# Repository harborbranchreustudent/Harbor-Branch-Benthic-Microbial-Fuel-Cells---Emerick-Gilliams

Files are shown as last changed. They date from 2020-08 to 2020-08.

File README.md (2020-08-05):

# Harbor-Branch-Benthic-Microbial-Fuel-Cells---Emerick-Gilliams
This repository holds all information relevant to the Benthic Microbial Fuel Cell (BMFC) Project with Intern Emerick Gilliams and Dr. Jordon Beckler

I urge you to read through the Final Project Write Up before looking through the GitHub files.

All of the following information is present in the Final Project Write Up:
• Detailed Relevancy, Methods, and Results of Indoor BMFCs... 
• Detailed Methods and Results of Outdoor BMFCs...
• Materials, Procedures and Recommendations regarding building an Arduino Voltmeter and an Arduino Waterproof Enclosure...
• Materials, Procedures and Recommendations regarding building your own BMFC Design and deploying it indoors and outdoors...

On the GitHub, you will find the different variations of code for the Arduino Voltmeter that was custom created. The information regarding these files are all in the Final Project Write Up.

A quick summary of these files are: 
They are all for an Arduino Pro Mini 3.3V 8MHz. 
Voltmeter_SD_RTC2_Sleep_Mini is for a single input;
Voltmeter_SD_RTC2_Sleep_Mini_Double is for a double input;
Voltmeter_SD_RTC2_Sleep_Mini_Triple is for a triple input;
Voltmeter_SD_RTC2_Sleep_Mini_Double_Charging is to be used with a double input for charging and discharging tests (More information on this in the Write Up.);

Download the three folders DS3232RTC, Time, Streaming and place into your libraries folder in your Arduino folder in order to use the files above. 

On this GitHub is also a supply list that lists everything you need to recreate my project.There are also the files and images of the circuit diagrams for all of the relevant codes. Once again, these are explained further in the Final Project Write Up. 

If you have any questions please reach out to me at gilliamse@ufl.edu...

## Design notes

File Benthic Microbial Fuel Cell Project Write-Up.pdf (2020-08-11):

# Benthic Microbial Fuel Cells Project

### Summer, 2020

Author: Emerick Gilliams
Supervisor: Dr. Jordon Beckler

# Table of Contents

OVERALL PROJECT SUMMARY AND INTRODUCTION: | 3
MY INDOOR FUEL CELLS | 4
WHY CREATE INDOOR BMFCS? | 4
MY VARIABLES | 4
Why These Variables | 4
Container Setup | 5
DATA GATHERING AND ANALYSIS | 5
Daily Voltage Readings | 5
Other Data Collection | 5
RESULTS | 6
Daily Voltage Measurements | 6
Discharging Tests | 7
Charging Tests | 8
MY OUTDOOR FUEL CELLS | 9
DATA COLLECTION: | 9
RESULTS: | 9
MATERIALS: | 11
MATERIALS FOR A DEPLOYABLE FUEL CELL: | 11
The Electrode System | 11
Fuel Cell PVC Design | 12
MATERIALS FOR ARDUINO CIRCUITRY AND ENCLOSURE | 12
Arduino Circuitry | 12
Arduino Enclosure | 13
MATERIALS FOR FUEL CELL DEPLOYMENT | 14
Variables | 14
Indoor Deployment | 14
Outdoor Deployment | 15
PROCEDURES | 16
ARDUINO RELATED PROCEDURES | 16
Arduino Material Modifications | 16
Arduino Circuitry Construction | 17
Programing the Arduino | 19
Calibrating the Arduino Voltmeter | 22
Testing and Measuring with the Arduino Voltmeter | 22
Monitoring Multiple Fuel Cells | 22
Conducting Discharging and Charging Tests | 24
Finding the Active and Sleep Current of the Arduino Circuitry | 25
Powering the Voltmeter via Battery | 25
Building the Arduino Enclosure | 26
FUEL CELL RELATED PROCEDURES | 28
Creating a Deployable Fuel Cell | 28
Indoor Deployment | 31
Outdoor Deployment | 33

RECOMMENDATIONS | 35
GENERAL RECOMMENDATIONS | 35
Variable Selection | 35
Fuel Cell Design (Unchambered vs. Chambered) | 35
Deployment is Key | 35
INDOOR DEPLOYMENT RECOMMENDATIONS | 36
Data Collection and Analysis | 36
Polarization Curves | 36
Oscillating Tests | 36
CLOSING REMARKS | 38

# Overall Project Summary and Introduction:

Hello!

My name is Emerick Gilliams, and I am a rising junior studying chemical engineering at the University of Florida. During the summer of 2020, I was taken on as a renewable energy intern at Harbor Branch Oceanographic Institute where I worked remotely on benthic microbial fuel cells (BMFCs).

BMFCs are an emerging option for renewable energy. BMFCs utilize microbes in the sediment of the benthic layer in a body of water to create an electric current as the microbes oxidize organic and inorganic matter. This creates a redox gradient between the anoxic sediment and oxic water.

The importance of this research and all research with BMFCs strongly relates to oceanographic research, as BMFCs are being investigated as a possible power source for subsea sensors. BMFCs are currently being used as battery substitutes and battery chargers for offshore dataloggers and sensors. Successfully making BMFCs a consistent power source would reduce the costs for device deployment, maintenance, and replacement, which happens to be some of the most expensive portions of marine research.

The overall goal of my project is to explore the capabilities of small-scale BMFCs. During my project, I have created ten indoor BMFCs using sediment and water samples from a nearby lake. I have been testing various sets of three variables: salinity, BMFC design, and addition of carbon-based additives. My project has shown that with even a fuel cell design size of a few inches, harvestable power is accomplishable.

During this research, I have also been working with Arduino circuitry to create a battery-powered device that can monitor the voltage of a fuel cell while recording that data to a micro SD card. This device can monitor up to six BMFCs for about 100 days while connected to a battery. Various code for the device can be found on the projects GitHub: Click Here... (https://github.com/harborbranchreustudent/Harbor-Branch-Benthic-Microbial-Fuel-Cells---Emerick-Gilliams)

For the conclusion of my project, three BMFCs were constructed in situ in a nearby lake and was monitored by my Arduino circuit in a waterproof enclosure. The data was analyzed after the completion of the program.

In this document, you can find information regarding:

- Materials required to make anything in my project….
- The procedures I created for my project…
- Detailed write-ups and data on each part of my project…
- Recommendations for anyone looking to follow in my footsteps…

Let us begin!

# My Indoor Fuel Cells

This part of the document is dedicated to my indoor fuel cells used in my project from the summer of 2020.

You will find the reason why I constructed these, the variables I used, how I collected data, and the results from that data.

For how I constructed these and pictures what they look like, check the procedures section.

### Why Create Indoor BMFCs?

There are a couple reasons why you would want to make indoor BMFCs.

The main reason is to control variables you cannot control in the environment. For example, one of the variables I tested was the effects of salinity. I would have never been able to do this if I were setting up my BMFCs in situ. Adding salt (or chemicals if you want to test the effect of that) can and will affect the environment you are testing in. Furthermore, do you know how much salt would be needed to change the salinity of an entire body of water? The only reasonable option for certain variables would be to create an isolated and easily changeable environment; Hence, create yourself a set of indoor BMFCs!

Of course there are other reasons, such as not having access to a good body of water to test in or wanting to test multiple variables at the same time; however, the main benefit is creating an isolated and changeable place to deploy your BMFCs.

### My Variables

During my project, I tested three different variables:

1. Salinity
2. Fuel Cell Design
3. Carbon-Based Additives

Why These Variables…
We tested the only two levels of salinity: freshwater from a lake and simulated ocean water. The simulated ocean water was taken from the same sample as the freshwater except for the addition of sea salt in the ratio of salt-to-water that would be found in the ocean. These two levels were chosen since most BMFCs were deployed in the ocean, and the nearest body of water to the location of the project at the time was a lake. An interesting project could be created around testing multiple levels of salinity though!

We also only tested two different fuel cell designs. The designs were the same excluding the fact that one had a chambered anode and one had an unchambered anode. This was done since these are the two classifications of BMFC design. See the

Fuel Cell Related Procedures regarding what these designs looked like.

The final variable was the addition, or non-addition of carbon-based additives to the bottom of the fuel cell container. This was done to see if the additives would encourage bacteria growth at a quicker pace, leading to a stronger voltage, than if no additive were added.

Container Setup…
I set the variables up in the following five combinations with two replicates each:
1. Freshwater/Chambered Design/Additive
2. Ocean Water/Chambered Design/Additive
3. Ocean Water/Chambered Design/No Additive
4. Ocean Water/Unchambered Design/No Additive
5. Ocean Water/Unchambered Design/Additive

You may be asking why I only had one freshwater group. The reason for this is I had eight possible combinations of variables, and I wanted to have two replicates each. One of the downsides of indoor BMFCs is you must have the space to place them. I only had the space for ten fuel cells, so three possible variable combinations had to be discarded.

After review, it was obvious that salt water would be a better environment for BMFCs due to the increased ionization in the water around the BMFCs. Due to this project being remote and the desire to strong results, Dr. Beckler and I decided to do mostly saltwater fuel cells.

### Data Gathering and Analysis

Daily Voltage Readings…
The main data that I gathered during my project was the daily voltage readings using a multimeter with leads connected to the anode and cathode. This was done twice a day at 10 AM and 4 PM. I find that this was unnecessary and that once a day is sufficient for future projects. These numbers gave an idea on how developed the redox gradient was at the time of measurement.

You can expect anywhere between 400 mV and 600 mv for a strong BMFC. In even the most ideal settings, the strongest redox potential you will see is 1.2V, so do not be disappointed by low voltages! Some of my fuel cells began with a negative voltage and slowly moved to positive over time. I began testing my cells the day after they were constructed, and I was already getting some interesting results.

Other Data Collection…
There are other tests you can run to gather data from as well. In the results section, there are some graphs regarding what I called “discharging” and “charging” tests. In the discharging test, the cathode and anode were set in series with a resistor. The voltage was monitored over a period and then plotted to observe the behavior of the fuel cells when discharging. This process is actually very important for constructing a polarization curve, something I never had the opportunity to do. See the Recommendations for more information on polarization curves.

The charging test was the exact opposite of this. The fuel cell would be discharged completely by touching the cathode and anode together, then the fuel cell would be monitored while the voltage increased back to its current high point, which is the same as that days daily measurement voltage values.

Both these tests can be done with the custom-made Arduino circuit and the “Voltmeter_SD_RTC2_Sleep_Mini_Double_Charging_Test” code. This code will monitor the fuel cell and record a measurement every 10 seconds. Make sure to calibrate and test on batteries to make sure it is accurate!

One test I never conducted but is very interesting to conduct would be an oscillating circuit. See the Recommendations.

### Results

Daily Voltage Measurements…
The following graph shows the daily measurements taken twice a day. Although some fuel cells started in the negative, a large majority of the fuel cells showed strong steady growth over the testing period. The highest points are in the low 600 mV range. The downward spike of the highest performing fuel cells near 7/7/20 was due to testing done on the cells that lowered the voltage temporarily. The three worst performing fuel cells were salvaged at a certain point as the materials were needed to construct the three in situ fuel cells used later in the project. This is seen in both graphs.

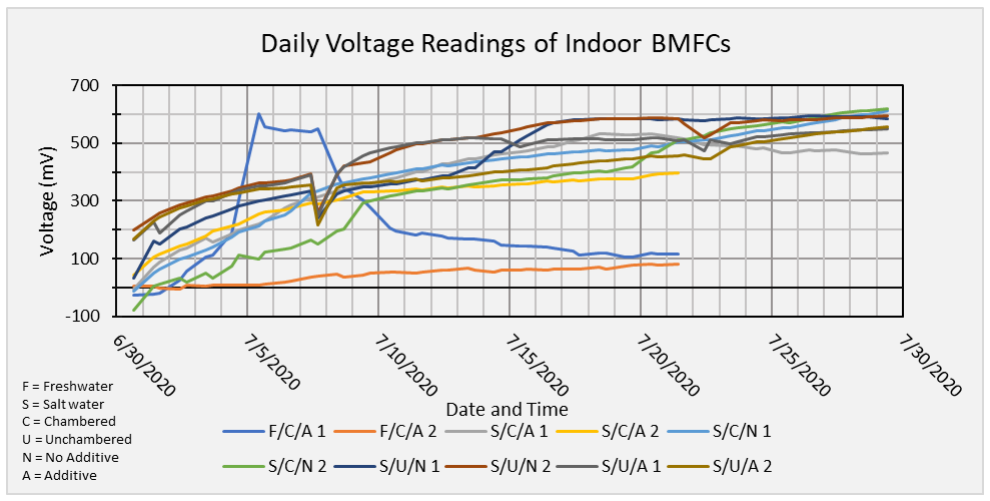
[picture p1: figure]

The following graph shows the daily measurements, but the replicates are grouped and averaged into their variable sets. From this you can see that the freshwater cells are the least consistent, while the saltwater cells are all consistently strong and steadily growing. This is most likely due to the increased ionization in the fuel cells with saltwater. The simple conclusion is saltwater fuel cells are stronger and a better option than freshwater.

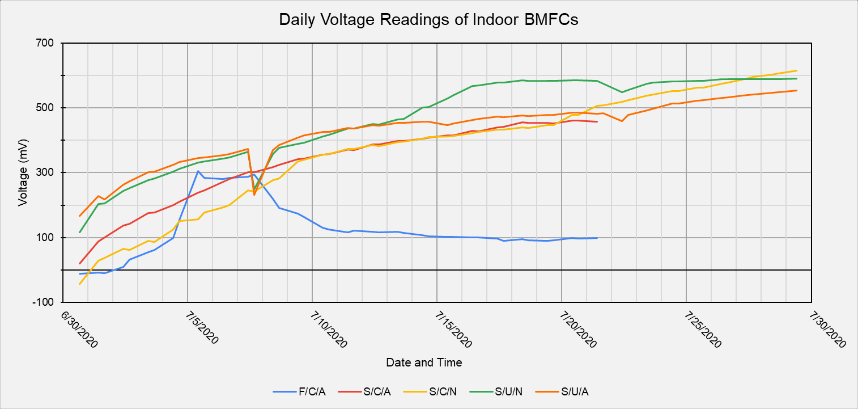
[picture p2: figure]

You can also see that unchambered vs chambered are generally the same, but with the slight advantage to the unchambered designs. This leads to the conclusion that the real variable here is ease of deployment. The easy the design is to deploy, the better chance the electrodes will be setup properly. The unchambered design is extremely easy to deploy in an indoor fuel cell, which many have given it the slight advantage it is shown to have. The chambered design would be easier to deploy in situ since the sediment in situ is much more compact, making it more difficult for an unchambered design to pierce the sediment.

The final variable, the carbon-based additive, seems to have little to no effect on the overall fuel cell voltage over longer periods of time; However, if you look at the first two weeks of deployment, you can see slight advantages to the fuel cells with additive. Coincidentally, the additive used was a 14-day slow-release vacation fish food. There may or may not be a connection. More testing needs to be done. There is no negative to adding an additive, only a possible benefit in having higher voltages earlier on. I would recommend the use of an additive if possible.

Discharging Tests…
This data was taken by placing a 20k Ohm resistor in series with the cathode and anode. The voltage was then measured across the resistor for 30 minutes and plotted. The four strongest fuel cells were fuel cells 7-10, which is why they were chosen for this test.

As you can see, the fuel cells will rapidly lose their charge and then stabilize at a lower voltage after a certain period. That stabilization voltage is the value needed to construct a polarization curve, which was not known to me at the time of the test. See the Recommendations section for more information.

The starting voltage is purely dependent on how developed the fuel cell is. The starting voltages coincide with the daily voltage reading of the day of the test.

This test was taken by recording a multimeter, but if you would like to do a test like this, use the code that is described in the “Other Data Collection…” section.

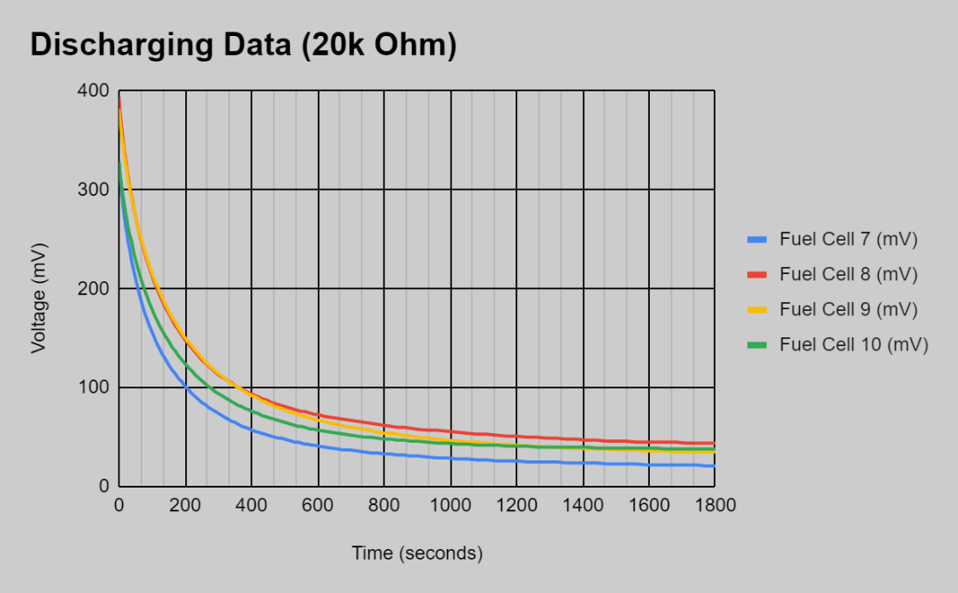
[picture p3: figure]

Charging Tests…
This data was taken by the code described in the “Other Data Collection…” section. The two of the strongest fuel cells at the time of testing was Fuel Cell 7 and 9. They were also chosen in a pair due to their proximity on the physical workstation.

As you can see, the charging behavior is very similar to the discharging behavior, as there is rapid change in the beginning and slow change as time goes on.

The test was stopped after 10 hours but could have continue to reach a better stabilizing voltage.

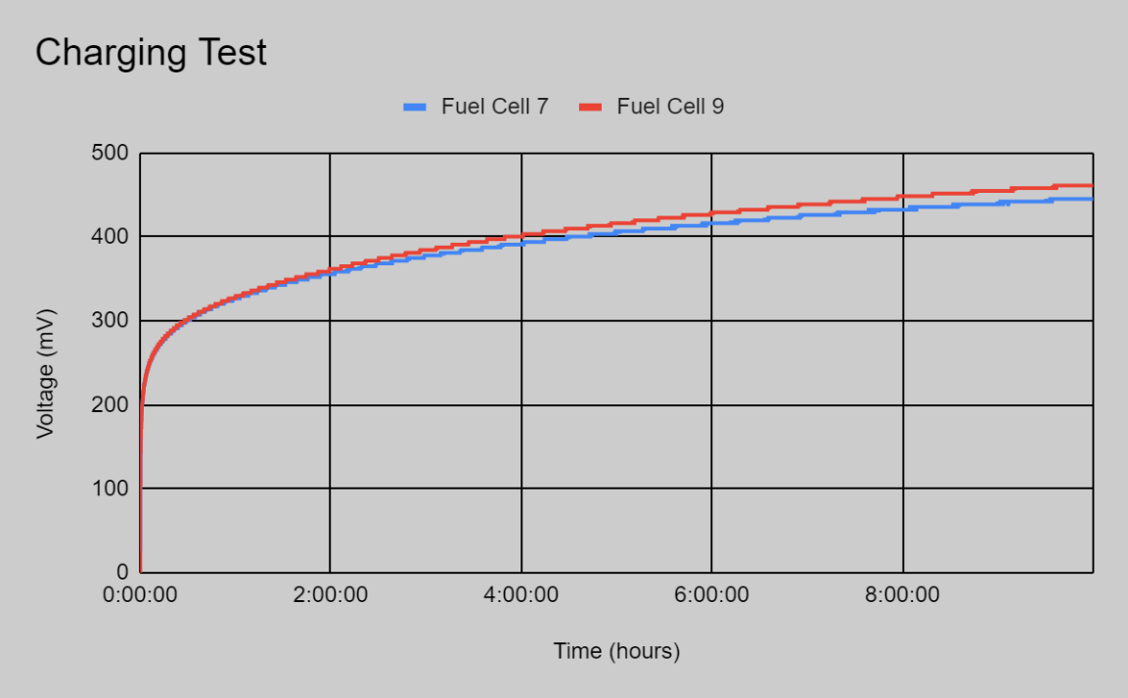
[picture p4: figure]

# My Outdoor Fuel Cells

### Data Collection:

Three fuel cells were deployed in a lake near me at the time. These fuel cells were being monitored by the custom-made device that is described further in the document. The fuel cells were deployed for slightly under a week before they were retrieved.

The device measured the voltage in mV every 10 minutes for the entire time. This data was transcribed onto a micro SD card for later analysis.

### Results:

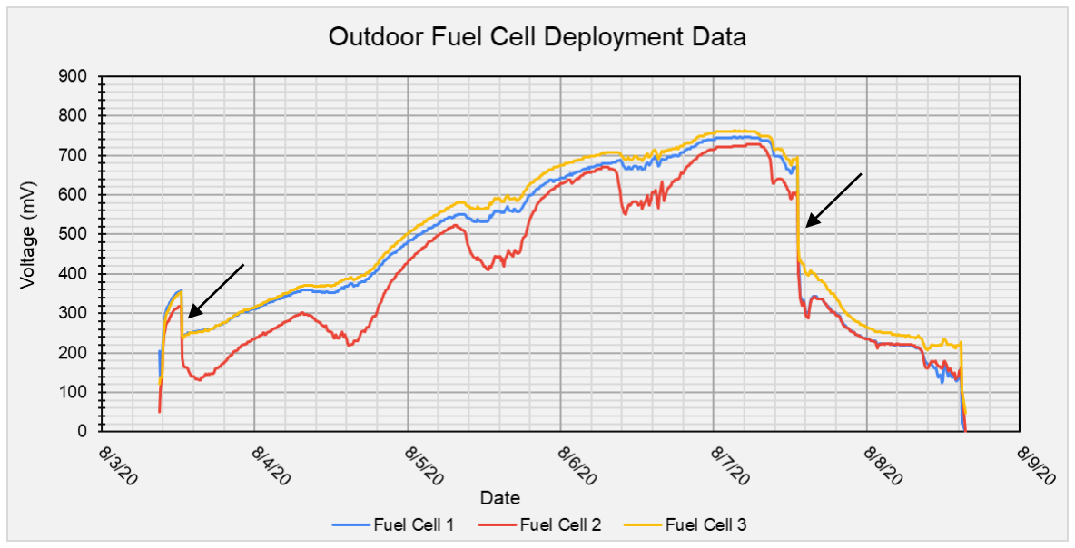
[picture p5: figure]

The graph above is the data for the outdoor deployment.

The first thing to discuss are the issues with deployment and how it affected the data.

I checked the state of the fuel cells every 1-2 days. When I went to check a day after deployment, Fuel Cell 2 was floating. I decided against redeploying the cell for these reasons.

1. I was uncertain if the data collector was fully operating due to a previous deployment issue.
2. if the measuring device was operating correctly, I did not want to disturb the sediment and affect the data collection.
3. I had two more, so I considered losing one was not an issue.

A few days after Fuel Cell 2 became dislodged, Fuel Cell 1 also began to float. You can see the effect of these changes on the voltages when looking at the two black arrows on the plot. The left most arrow is showing when Fuel Cell 2 dislodged, and the right arrow is Fuel Cell 1.

Now, why are the voltages all about the same and follow the same patterns even though fuel cells were dislodging?

I believe this is due to the concept that when multiple BMFCs are in the same body of water, they act as one BMFC.

As you can see, on the day Fuel Cell 2 dislodged, the red line dipped the strongest and was always under the other two lines. It also affected the overall voltage growth as you can see all the lines were increasing at a high rate in the beginning, then that rate decreased after the first dislodge. As time went on the yellow and blue lines both stayed about the same, with the red line being consistently worse.

It appears the lines were going to plateau at around 800 mV when the other fuel cell dislodged causing the voltage to drop significantly again. The overall plateau also decreased to around 200 mV. Furthermore, the fuel cell that dislodged next (Fuel Cell 1) then joined the red line and was the same until they were pulled from the sediment.

Another interesting thing that happens is every day at the same time there are periods of instability in the voltage. Furthermore, both fuel cells dislodged at a time during this instability. My guess is it has to do with the movement patterns of life in the lake. It makes sense that an increased amount of movement around the BMFCs would affect the voltage. It also makes sense that increased movement around the BMFCs could have jostled them enough to dislodge them from the sediment.

Interesting conclusions:

1. Supporting evidence that all BMFCs in a single body of water act as one BMFC.
2. If a BMFC dislodges, it will still hold a voltage, but one slightly lower than the ones still in the sediment
3. The amount of BMFCs in the sediment determines the overall maximum voltage.
4. If all fuel cells stayed in place, we could have gotten a value well over a volt in all cells, which is very interesting since the highest we saw in a month of indoor testing in environments with salt and additives is only around 625 mV.
5. Movement of life around the fuel cells could have cause periods of instability.
6. Make sure future BMFC designs are not buoyant to avoid unintentional dislodges.

# Materials:

All materials that are listed can be found in the Supply List.

This section is divided into categories for each part of the project, so some materials are listed multiple times if needed for different sections. Make sure you double check to not order things multiple times!

That supply list will give you an estimated cost for each item suggested, and a link or description of where you can find one!

For the sake of simplicity, we are going to use the symbol X to represent the number of BMFCs you would like to create.

For example, in my project X = 10.

If you see an [X * #] that is the quantity needed. No brackets imply 1.

### Materials for a Deployable Fuel Cell:

The Electrode System…
We are first going to list the materials for what I call the “electrode system” (For me, X = 10):
1. [X * 2] Electrodes
a. I used Carbon Fiber Brushes from Mill-Rose. I highly recommend these electrodes if your budget allows it. I used 2-inch brushes with 1-inch bristle length and 1-inch bristle radius
2. Electrical Wire
a. If you have the chance, get two colors! Black and red works perfectly!
3. Soldering Kit
a. The one I linked came with wire strippers and tweezers; if you decide to buy a different one, purchase these as well.
4. Wire Quick Connect Kit
5. Epoxy
6. Heat shrink tubing
7. Heat Gun
8. Multimeter
a. Test your connections every time you solder, epoxy, or connect wires!!!!
9. Pack of AA batteries
a. Use these with your multimeter or Arduino to test your connections or code/circuit.
10. Rosin Core Solder
a. In the Arduino Purchase section...
11. Painters Tape
12. Cling Wrap
13. Small zip ties
14. Pliers.

15. Some type of PVC to hold your electrodes (I used the ¾ inch PVC)
a. Mine is listed in the Fuel Cell PVC Design Section
16. Cardboard from boxes items came in

These materials are all highly recommended and should be purchased if you want to recreate the project.

Fuel Cell PVC Design…
These materials are for the PVC housing you that hold your electrodes system.

Depending on the design you chose, this will be different. I listed my materials if you wish to replicate my design exactly. See the Recommendations section…

For my 10 fuel cells, I had 6 chambered designs and 4 unchambered designs.

Here are the materials I used for my unchambered design (X = 4):
1. 3/4-inch diameter PVC pipe segment
2. [X] 3/4 elbow PVC pipe
a. I recommend using a vertical coupling if you have enough space in the enclosure. I used the elbows, so they are what are listed.
3. PVC pipe cutter

Here are the materials I used for the chambered design (X = 6):
1. 3/4-inch diameter PVC pipe segment
2. [X] 3/4 elbow PVC pipe
3. PVC pipe cutter
4. 3-inch diameter PVC pipe segment
5. [X] 3-inch x 1.5-inch PVC Coupler
6. [X] 1.5-inch x 3/4-inch PVC Bushing
7. Hacksaw
8. Sandpaper (The coarser the paper, the better.)

Once again, all these materials are subject to change if you use a different design.

### Materials for Arduino Circuitry and Enclosure

Arduino Circuitry…
1. Micro SD Card reader
a. Needed for the circuit to save the data it is monitoring
2. Micro SD Card
3. M-F, F-F, M-M Wires Kit
a. Needed for certain connections. Does not hurt to have extra wires either.
4. Pre-Formed Jumper Wire Kit
a. Needed for most connections. Keeps breadboard clean and easy to organize.
5. DS3231 Real Time Clock a. Needed to allow Arduino to log the time measurements were taken
6. Battery for DS3231
7. Arduino Pro Mini 3.3V 8Mhz
a. Arduino of choice for the circuit.
8. Rosin Core Solder
a. In Electrode Materials
9. Breadboards
10. Lithium Polymer Battery Connector
a. This makes plugs into the charger and allows you to connect it to breadboard
11. Lithium Polymer Charger Circuit
a. This makes the battery connection safer and allows charging if needed
12. Lithium Polymer Battery
13. FDTI Breakout
a. This allows the communication between the mini and the cable. Needed for programming.
b. Get the circuit that matches the voltage of the Arduino Pro Mini you have. Mine were both 3.3v, and that is what I recommend.
14. FDTI Cable
a. This allows the communication between the breakout and a PC or laptop. Needed for Programming.
15. Header pins

Arduino Enclosure…
This is the materials you need to construct the enclosure for the Arduino to go underwater. Please pay attention to the actual design of the enclosure. The number of penetrators, thruster cable lengths, and blanks depend on how many cells you are testing.
1. Potting Kit
a. Needed to apply the epoxy to the penetrators.
2. Marine Epoxy
a. Needed to seal the penetrators
3. M10 Cable Penetrator for 6mm Cable
a. Needed to pass the cables through the enclosure cap.
b. For 1 fuel cell to be monitored: 1 Penetrator needed
c. For 2-3 cells: 2 penetrators needed
d. For 4 cells: 3 penetrators needed
e. For 5-6 cells: 4 penetrators needed
4. Penetrator Wrench
a. Used to tighten the penetrators
5. M10 Cable Penetrator Blank (No Hole)
a. Needed to fill the empty holes in end cap
b. For 1 fuel cell to be monitored: 3 blanks needed
c. For 2-3 cells: 2 blanks needed
d. For 4 cells: 1 blank needed
e. For 5-6 cells: 0 blanks needed
6. 1 Meter of Thruster Cable (3 conductors, 18 AWG)
a. Same amount of lengths needed as penetrators.
b. Adjust length if you want more space between cells.
7. 200 mm of Customizable Cast Acrylic Tube (4″ Series)
8. Aluminum End Cap with 5 Holes (4″ Series)
9. 2 O-Ring Flanges (4″ Series)
a. Needed for both sides
10. Aluminum End Cap (4″ Series)

11. Enclosure Vent and Plug
a. Needed for all enclosures. Cannot skip.
12. Silicon Grease
13. Hex Driver
14. Exacto Knife
a. Needed to strip thruster cable.

### Materials for Fuel Cell Deployment

Variables…
These final materials are based on what variables you test. I tested Salinity, Chamber design, and the addition of a Carbon based additive.

For salinity:
1. Salt

For Chamber design:
Look at previous section

For Carbon-Based Additive:
1. Vacation slow release fish food

Indoor Deployment…
These are the materials needed to deploy your fuel cells into indoor containers. For me, X = 10. If you are deploying your fuel cells outdoors or in situ, you may not need these materials.
1. [X] Deployable Fuel Cell
a. You need something to deploy obviously. Consult the electrode system materials/PVC housing materials to find out what you need.
2. [X] Plastic Containers for the fuel cell
a. You can find cheaper ones not on amazon
3. [X * 0.5] Air Pumps
a. I only need 5 since the pumps I got were double tubed. HIGHLY RECOMMEND DOUBLE TUBED.
4. Power strip
a. To plug the Air pumps into. If you need more than 6 air pumps, pick a strip that fits your needs.
5. Painters Tape
a. In Electrode System materials…
6. Shovel
7. 2 Large 17-gallon bins
8. Cardboard from boxes items came in
a. Same as from Materials for Electrode System. Recommended if you do not have workstation.

If you are deploying indoors, you will want to actively test and collect data. This is what you will want.
1. Multimeter
a. Same as Electrode System section
2. Alligator Clip kit

3. Variable Resistors/resistor kit
a. You will need these to conduct discharge tests or polarization curves. See Polarization Curves… and Data Gathering and Analysis.
4. Completed Arduino Circuit
a. Helpful to have for discharging and charging tests. Not needed though. See Arduino materials for what you need for that.

Outdoor Deployment…
These are the materials for outdoor deployment.
1. [X] Deployable Fuel Cell
a. You need something to deploy obviously. Consult the electrode system materials/PVC housing materials to find out what you need.
2. Completed Arduino Circuitry
a. Needed to monitor your in-situ cells. Consult the Arduino Circuitry Materials
3. Completed Arduino Enclosure
a. Needed to keep your circuit waterproof. Consult the Arduino Enclosure Materials
4. Cinderblock or weight of some kind
a. Needed to weigh down the completed enclosure.
5. Something to loosen the sediment
a. Optional, but very helpful. I used an extra PVC pipe sediment to stab at the sediment to loosen it.

# Procedures

### Arduino Related Procedures

Arduino Material Modifications…
The first step before modifying the modules is to understand why.

These modifications were made to lower the current consumption to extend the battery life.

After the modifications, the current during sleep mode of both the triple input, double input and single input circuit is 0.8mA.

After the modifications, the current during active measurement is 4.8mA for a single input, 5.0mA for a double input, and 5.2mA for a triple input.

Why the following modifications were made:
DS3231 Real Time Clock Module:
- Removal of the diode in the top left of the module...
- This was removed to disconnect the trickle charge current that goes into the battery socket which attempts to charge the battery.
- I recommend the use of a CR2032 3V Lithium Coin Battery. If you use this battery,
the trickle charges the module is attempting to provide can explode the battery.
- If you decide to use a rechargeable battery, you can keep this. I suggest against using the rechargeable battery over the CR2032 3V Lithium Coin Battery.
- Removal of the Power LED in the bottom left of the module...
- This was removed to lower the power consumption of the module in sleep and
active mode, as the power LED is always on.
- The removal of this saved about 2 mA in sleep and active mode. This is a must remove to maximize power consumption.
Micro SD Card Module:
- Removal of the AMS1117 Voltage Regulator...
- This is a must remove IF you are using a 3.3V, 8MHz, Pro Mini Module (Or any Arduino/Microcomputer setup operating at 3.3V).
- Micro SD cards operate at 3.3V originally. The Micro SD module used in the project has a voltage regulator that takes a 5V input from an Arduino/breadboard/source and regulates it to a 3.3V for the SD card.
- Since we are operating at 3.3V, this regulator will not work correctly. This is a MUST remove if operating under these conditions.
Arduino Pro Mini
- Removal of the Power LED...
- This was removed to lower the power consumption of the module in sleep and active mode, as the power LED is always on.
- The removal of this saved about 2 mA in sleep and active mode. This is a must remove to maximize power consumption.

Supplies to make the Modifications:
Supplies Needed:
1. Heat Gun
2. Insulated Tweezers (Should have come in your soldering kit)
3. Soldering Iron
4. Rosin Core Solder

How to make the Modifications:
The removal of the components is relatively easy! All components follow the same steps to be removed from the PCBs (Printed Circuit Board).
1. Plug in Heat Gun
2. Turn on Heat Gun
3. Use Heat Gun to warm the ENTIRE board.
a. The board does not need to be as hot as the component you are heating, but it is helpful to heat the whole board slightly.
4. Focus the Heat Gun on the component you are removing with one hand and pick up the tweezers with the other hand.
5. Either pick up the component with the tweezers once the solder is warm enough, or you can just knock the component off its pads by tapping it if there is enough room.
6. Turn off Heat Gun

This is all you need to do for all the modifications excluding the Micro SD Module.

For the Micro SD Module, after removing the regulator, the voltage input and output pins need to be connected.

For the AMS1117 module on my Micro SD Module, here is the relevant pinout. Your Micro SD Module may be different so double check!

Since the relevant pads for the AMS1117 module were next to each other, I connected the pads with a solder blob. It is ugly, but it works.

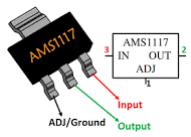
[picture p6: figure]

Make sure you double check the model of regulator you have before doing this to make sure you know which pads are which!

Arduino Circuitry Construction…
This is much easier than it sounds if you have never done this before.

Here is my favorite Pro Mini Pinout. Very Useful!!! Pro Mini Pinout… (https://cdn.sparkfun.com/assets/c/6/2/2/1/ProMini8MHzv2.pdf)

The hardest part is soldering together the Pro Mini if it is unsoldered. Here is a tutorial on how you can do that: https://www.youtube.com/watch?v=37mW1i_oEpA. I suggest using some vertical header pins instead of the right-angle ones you were probably given with your Pro Mini. This will make it easier to program the Arduino. You will also need to solder the A4 and A5 pins to use the Real Time Clock, and the A6 and A7 pins if you want to monitor 5 or 6 fuel cells (Not all Pro Minis have these pins, but mine did).

The picture below is the circuit diagram of the voltmeter that measures a SINGLE fuel cell. This is what you should build first after the modifications to your PCBs and you have soldered the Pro Mini. You can ignore the Red FDTI plug on the left connected to the Pro Mini. This will be addressed in the Programing the Arduino… section.

What if you want more than one fuel cell? Construct this first then you can add the additional wires at a later point after you verify that your circuit is working on a single fuel cell. The information for how to do this is in the Monitoring Multiple Fuel Cells… section.

The AA battery is only a placeholder and an example on how you would connect something you want to see the voltage of to the voltmeter. You can read more about this in Testing and Measuring with the Arduino Voltmeter….

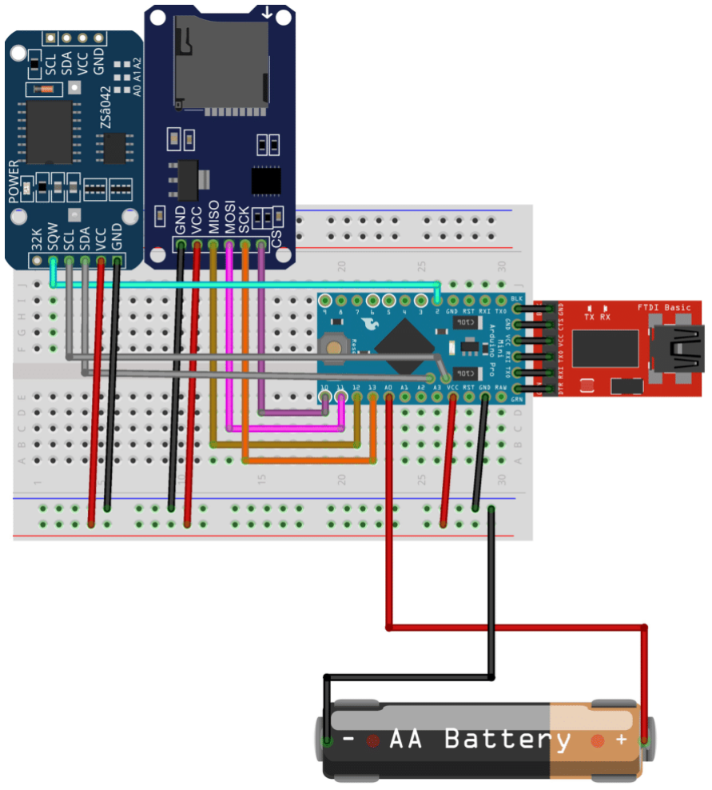
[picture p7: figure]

I am not going to give a detailed procedure on how to put this together. You literally just plug the wires into the right slots, and you are good to go. I have provided a couple pictures of my organized breadboard from different angles. This will give you an idea on how to organize yours. Feel free to copy mine. Keep in mind that the pictures being provided are for the Triple Fuel Cell Circuit. This means that you do not need as many wires coming from the ground or A0-A2. When looking at the pictures, you should imagine that the gray + black wires and the red + orange wires from the two wire triplets do not exist!

Expand the pictures for a closer look at row numbers etc.

The white and gray wire doublet is taped just to save space. These pictures are from right before inserting the circuit into its enclosure. Don’t worry, we’ll get there soon.

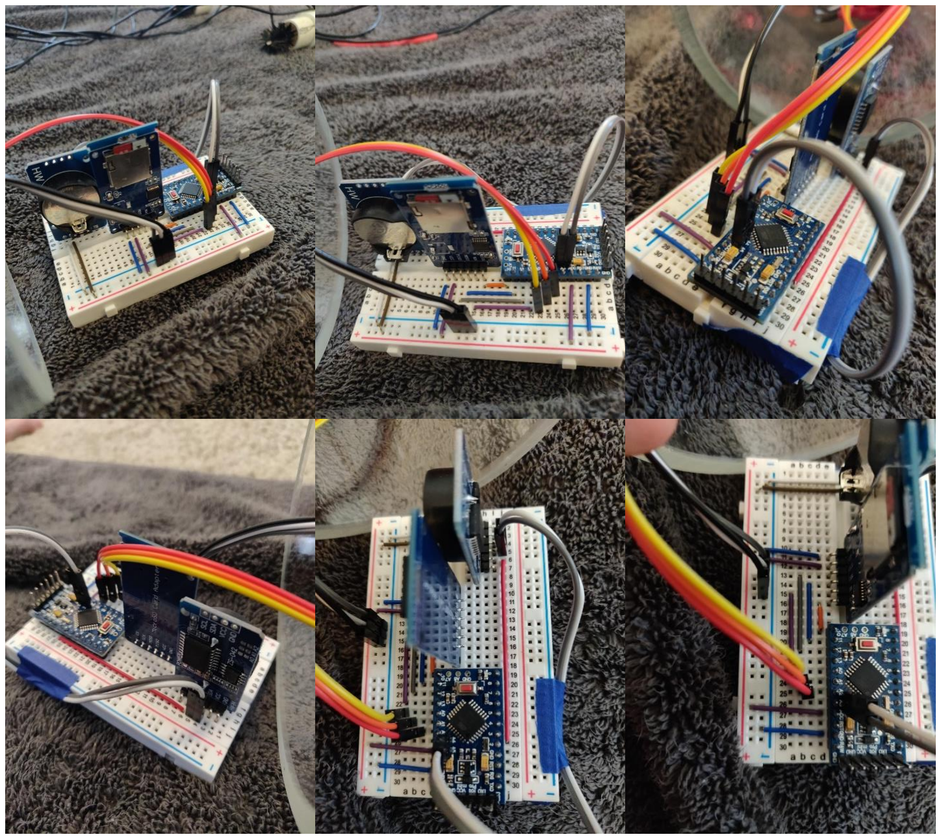
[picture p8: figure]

Programing the Arduino…
Before this section, I am going to preface that if you are having any issues with the beginning portion of this section, look up some online tutorials. They will explain things better than I can.

You will need to have a fully constructed circuit before attempting to program it. If you have not already done so download the Arduino IDE. I recommend the desktop offline version. Click Here... (https://www.arduino.cc/en/main/software)

Scroll down and select what operating system you are using.

After this is completed, DOWNLOAD THE REQUIRED LIBRARIES FROM THE GITHUB: Click Here (https://github.com/harborbranchreustudent/Harbor-Branch-Benthic-Microbial-Fuel-Cells---Emerick-Gilliams) for the files and click here (https://www.digikey.com/en/maker/blogs/2018/how-to-install-arduino-libraries) for a tutorial on how to actually put those libraries into the Arduino IDE.

To give you a general idea of what to do…

1. Download the Zip from the GitHub.
2. Extract the Zip
3. Place the entire folder in the “Arduino” folder.
4. Drag the three libraries into the “libraries” folder in the “Arduino” folder.
5. Now all your libraries are in the right place, and you have all the codes I created in your Arduino folder as well.

After that, you are going to want to plug your FDTI cable into your FDTI breakout circuit. The breakout will attach to your 6 Arduino Pro Mini FDTI pins. Use the image attached to the side to double check what pins go into what slots. My breakout matched my pins in reverse, so I had to attach it upside down. Make sure to double check!

After you do that, your Arduino Pro Mini should receive power. Make sure you are using the right port, processor, and board type in the IDE. This will cause issues, and I have made plenty of those mistakes! You should open the “Blink” example and
play around with the timing of the built-in LED to make sure the programmer
works.

If this is your first time messing with Arduino, just familiarize yourself with the IDE and understand the basics. Watch some tutorials on the basics like uploading and compiling.

I will say it again, if you are having any issues with anything up to here, I may have missed something. I am not an Arduino expert; I am a chemical engineering student. Look up some tutorials and I am certain it will fill in the blanks.

After all these steps, you just need to open my Arduino code called “Voltmeter_SD_RTC2_Sleep_Mini.” This will be the code that allows you to measure a single item, whether it is a battery or BMFC.

If you are curious with the naming of the code, this is the breakdown: The circuit is a Voltmeter that uses an SD module and the 2

nd Real Time Clock library I tried to use. It saves power using Sleep mode and it is compatible with the Pro Mini. Nothing too crazy there. You can probably guess what order I added things…

Here are the other circuit diagrams as well. The first diagram shows how you connect the LiPo to the circuit of the single input. All other diagrams have the LiPo connected as well

The next diagrams are for a double input, and the final diagram is the triple input.

The diagram files are all on the GitHub as well.

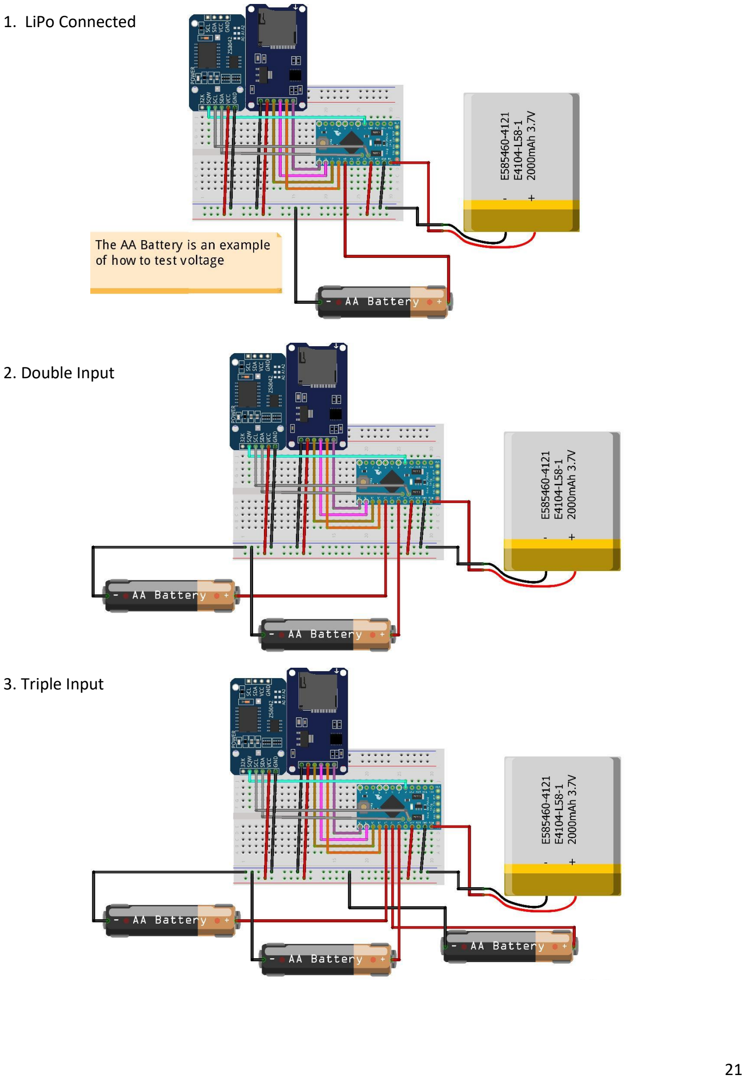
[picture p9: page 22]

1. LiPo Connected
3. Triple Input
2. Double Input

Calibrating the Arduino Voltmeter…
Now that your code is uploaded, you need to calibrate your voltmeter.

Calibrating your Voltmeter code to get accurate voltmeter readings is very easy!

All you must do is take the positive lead of a multimeter and connect it to the VCC pin either through a breadboard or directly. (I prefer using a wire connected to the same row as the VCC to connect my positive lead too.)

You then connect the negative lead to the ground of a breadboard (if connected to the Arduino ground) or to the ground on the Arduino directly. (I prefer a wire connected to the breadboard to connect my negative lead to.)

Read your Multimeter’s voltage reading. It should be near 3.3V if you have the 3.3V Pro Mini.

The voltage your multimeter is reading is what should be entered into the "Cali" variable in any of the codes I wrote.

Make sure to recalibrate when switching between like LiPos, PC USB slots, and other power sources.

Testing and Measuring with the Arduino Voltmeter…
After the construction and calibration of the voltmeter, you should test the voltmeter is getting the correct voltage readings. To do this, I would use the multimeter to check the voltage of an AA battery. If the battery is new, the voltage should be around 1.5-1.6V. You need a voltage source less than 3V since that is the maximum reading for the voltmeter you created.

Once you have a reliable reading from your AA battery, then take the positive lead (The analog pin wire) and the negative lead (The ground wire) and attach them to the positive and negative ends of the AA battery, respectively. To see your voltage reading, you must have the device being powered by your PC or laptop. The voltage reading will be shown in the serial window. If you are not getting a similar voltage reading, something is wrong with your design. Make sure your connections between the Arduino voltmeter and the AA battery/whatever you are testing are very secure. Do not be afraid to touch wire ends with your fingers.

Measuring your fuel cells is the same process. You connect the positive wire of the Arduino to the cathode of the fuel cell. You connect the ground wire to the anode wire of the fuel cell.

Monitoring Multiple Fuel Cells…
To monitor 2 or 3 fuel cells, you just need to upload the version of the code for either the double or triple input.

For the double input, use A0 and A2 as your analog pins. All you need to do change the single input hardware to the double input is add a new positive wire to the same row as A2 and an additional ground wire to the ground strip on the breadboard.

For the triple input, use A0, A1, and A2. To change from double to triple input, add the additional positive wire to A1 and an additional wire to the ground strip.

For monitoring more than three fuel cells, you must adjust the code. I will give you some of the things that need to be adjusted to change the triple input to a quad input. Changing from a quad to quintuple or sextuple input is the same changes. I will be referencing lines in the directions below, use the pictures provided, not your own code lines. Your lines will be changing as you add lines to your edited code.

- Add an additional float variable for input_voltage4 under “Voltmeter variables” around line 35.
- Add an additional line at the end of the following block before the close command. Copy and

paste 116 and 117 below it so there are now two duplicates of the comma and voltage (A2) lines right after each other. Change the top duplicate from println to print and change the second (A2) to the analog you are using for the next input (USE A3 OR CHANGE IN FOLLOWING DIRECTIONS).

- In the following lines, copy this under to line 149:
int analog_value4 = analogRead(A3);
input_voltage4 = (analog_value4 * (Cali)*1000) / 1024.0;
- Copy this to line 162:
if (input_voltage4 < 0.01) {
input_voltage4=0.0;
}

- Change the println to print on line 168 and copy and paste the following to 169: Serial.print(", ");
Serial.println(input_voltage4);

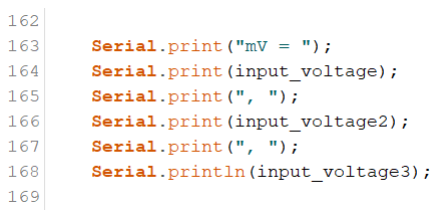
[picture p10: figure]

- Change the println to print on 224. Copy and paste the following so it is between 224 and 225. voltData.print(", ");
voltData.println(input_voltage4);
- Change the println to print on 249. Copy and paste the following so it is after 249. Serial.print(", ");
Serial.println(input_voltage4);

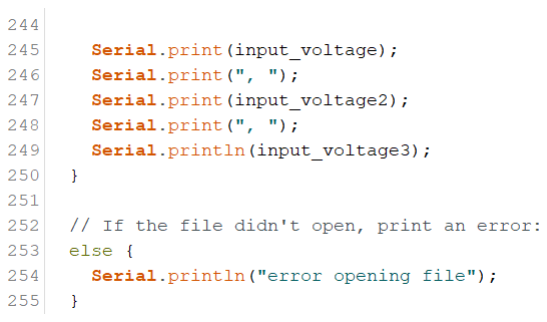
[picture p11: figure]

That is all the changes you should have to make. I may have missed something though since I did not have an actual chance to test these changes. Adding more inputs is not difficult and mostly copy and pasting what commands are needed to be followed for the previous analog pins 0-2. If you understand all the code, you should not even need these rough instructions.

For the hardware, you just need to add another wire to the additional analog pin being used as another input (For the recent instructions, it was A3) as well as another wire to the ground strip.

I think you can guess how to modify the circuit and code to add a 5th and 6th input.

Conducting Discharging and Charging Tests…
To conduct the discharge test, first connect the Arduino voltmeter leads to both sides of a resistor and turn on the device. Once the device is actively measuring the voltage over the resistor, you can place the resistor in series with the cathode and anode. Make sure the positive lead is on the side of the cathode and the negative lead is on the side of the anode. Use gator clips to secure the connections

The charging test is simple. Secure the positive lead of the Arduino device on the cathode wire and the negative lead on the anode wire. Turn the Arduino device on so it is recording data. Touch the cathode and anode wires together and hold them for a few seconds. This should drain the voltage of the fuel cell. Allow the fuel cell to build its voltage up and the device will monitor that for you.

You can see examples of my results for these tests in the Results section.

Finding the Active and Sleep Current of the Arduino Circuitry…
This is also not very difficult. To find the current draw of your circuit, you need to have your FTDI breakout and cable and some F-M wires with a single M-M wire.

Take 6 F-M wires and attach those to your Arduino Pro Mini FTDI pins. Plug your M-M wire into the VCC female header on the FTDI breakout. Insert the rest of the respective F-M wires that are attached to the Pro Mini so only one side of the M-M wire and the M side of the F-M wire connected to the VCC of the Pro Mini are not connected to anything.

You can now take some gator clips and attach the M-M wire to the positive lead of a multimeter and the M side of the F-M wire to the negative lead. Set the multimeter to the current reading mode of DC. Plug the FTDI cable into the breakout and PC.

You should see the active current when the Pro Mini is actively measuring (I changed the time interval of the code so the device would measure long to get a more accurate current reading). I got a 4.8 mA reading when using the single input. This is assuming you followed all the modifications and removed all the excess components from the PCBs.

You will see the sleep current when the device is not actively measuring. I got around 0.8mA for this.

Powering the Voltmeter via Battery…
To power the Pro Mini via battery, I used a 2000 mAh LiPo battery and a battery manager. I recommend these, but you can use different batteries. If using a LiPo battery, I highly recommend a battery manager to increase safety.

I plugged the LiPo into the BATT IN slot of the battery manager and then plugged in a non-connected JST wire to the SYS OUT slot of the manager. The wires of the JST connector were too thick to plug into the breadboard, so I created a plug out of 4 male header pins.

I first removed the middle two header pins with pliers. I then soldered the JST wires to the short end of the header pins. The battery can now be connected directly to the breadboard. 4 header pins were used as this is the perfect amount of space to insert the “plug” into the ground strip as well as the RAW pin of the Pro Mini. Make sure you plug the battery into the RAW pin and then wire the VCC pin to the positive power strip of the breadboard.

DO NOT PLUG BATTERY IN AS WELL AS USE THE FTDI BREAKOUT. THIS WILL DAMAGE YOUR PC AND CIRCUIT.

Building the Arduino Enclosure…
First watch these tutorials:
https://www.youtube.com/watch?v=G6PqEsKjxHM
https://www.youtube.com/watch?v=mKaJLWv1SCw

These should show you how to construct the enclosure, strip the thruster wires, and pot the penetrators. They explain it much better than I can. I will give you some things you should do while following the tutorials above that will help when recreating my enclosure:
- Strip the thruster cable so about 3 inches of wire are exposed on the other side of the penetrator when it is inserted fully.
- Before potting the penetrator, fully construct the end caps by attaching and tightening all of you blanks, penetrators, and vents. Then pot the penetrators while they are already inserted into the end cap. This will give you a sturdy place to pot them if you do not have a vice, and then you do not need to try and tighten them with a cable in the way.

To build the enclosure like I have, you will need 18-22 AWG wire quick connects. If you are reading this part, I am assuming that you have already potted the penetrators and have attached the O-rings to the end caps and vents by following the tutorials linked.

1. Decide which wires will be your cathode wires and which will be your anode wires…
a. For me, this was simple. I had three fuel cells, so three cathodes and three anodes. I denoted one of my two thruster cables cathode wires only and vice versa for the anodes. I then simply matched the colors to match a pair of electrodes.
b. I recommend cutting a red heat shrink in thirds (or in even pieces related to how many fuel cells you are measuring) so you have three heat shrink tubes you can shrink onto the three cathode wires. This will be very helpful in the future!
2. Attach the quick connects to the thrusters…
a. Attach the sockets (The quick connect that folds over the wire) onto all the thruster cables regardless of cathode or anode classifications.

3. Modifying jumper wires…
a. Since I was measuring three fuel cells, I used triplets stuck together of M-M wire.
b. Remove any plastic housing near the tip of M-M wires.
c. Slide the quick connect plugs (The ones that are crimped) onto the exposed metal points. Its okay if you use different color plugs and sockets, they all fit onto each other. Choose the plug that will be crimped easiest onto the exposed metal of the wire end.
d. Crimp these to the wire ends so you have two triplets of wires with one end that can go into the breadboard and one end that can be quick connected to the thruster cable.
4. Insert the modified wires into the breadboard…
a. I inserted one triplet into the A0, A1, and A2 analog pin
rows.
b. The other triplet was inserted into the ground strip.

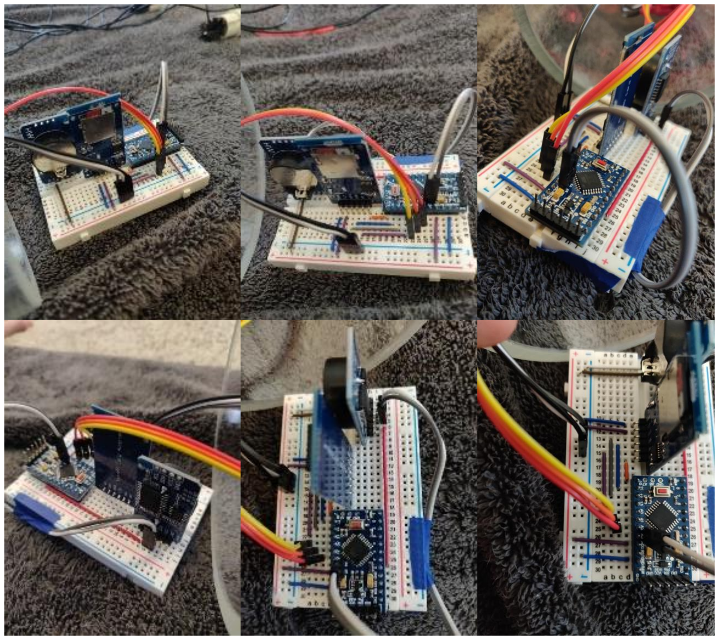
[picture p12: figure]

c. You can remove the wires that were acting as your Arduino voltmeter wires as well. So only the triplets are being used to measure voltage. See the images below. The Black-Gray-White triplet was for my ground and my Yellow-Orange-Red triplet was for my analog pins.
d. You can now connect the Pro Mini to the thruster cable by connecting the quick connects.
5. Secure the battery and charging circuit…
a. To save space, I taped the LiPo onto the bottom of an end cap. I then attached the battery manager circuit on top of that and had the battery plug attach to the breadboard from there.
6. Upload the proper code…
a. Depending on how many fuel cells are being deployed, upload the proper code to the Pro Mini and make sure it is running correctly on the PC.
7. Attach your fuel cells…

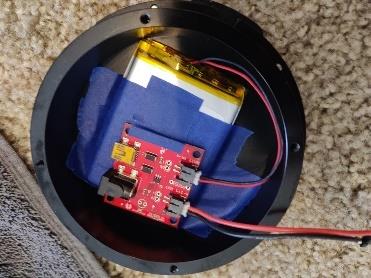
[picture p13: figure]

a. Solder and heat shrink your fuel cell cathode and anode wires to the other side of the thruster cables.
b. Keep your cathodes and anodes consistent!
c. I am not going into details for this part since it is entirely dependent on your fuel cell design.
8. Complete the enclosure…
a. Connect the quick connects and open the vent. Close the end cap with the penetrators over the acrylic tube.
b. Plug the battery into the breadboard and reset the Pro Mini to make sure the program is running correctly.
c. Close the battery endcap to completely close the enclosure tube.
d. Close the vent.
9. You are done!

a. The enclosure is completely closed and waterproof (if you followed the video tutorials above as well).

### Fuel Cell Related Procedures

Creating a Deployable Fuel Cell…
This entire procedure list is based on fuel cell design. Keep that in mind to adjust whatever you need to fit your design!
1. Prepare your brushes and wires for soldering…
a. For this you should cut your wires to a uniform length (2-3 feet is sufficient) and strip the ends.
b. If you have different colors of wire available, Great! You should decide on half of your electrodes being cathode and half being anode. Simply assign one color wire for each and use those wires with the respective electrodes you want designated as anode or cathode. If you only have one type of wire color, no worries! We will address this in future steps!
c. I twist the exposed wires to create a more uniform strand.
d. Wrap the wire around the electrode stem and solder them together.
e. Put to the side and let cool while you do the next one.
f. After you complete the next wire-brush connection, move the cooling brush into a storing box and move the new wire-brush to the cooling spot.
g. Repeat this until all brushes are soldered.
h. Make sure to test your connections with a battery and multimeter!

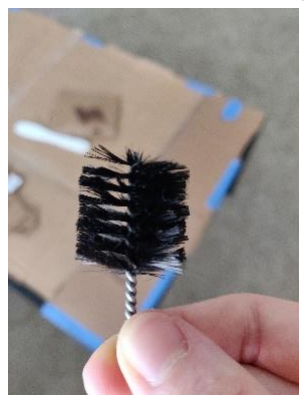
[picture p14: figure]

2. Cut your PVC pipes…

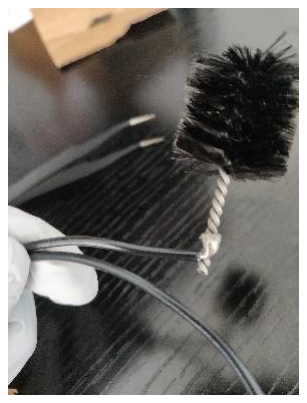
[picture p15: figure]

a. According to your design, cut the ¾ inch PVC pipe and 3-inch pipe to your desired height.
b. I cut my ¾ inch PVC into 5/4-inch lengths and my 3-inch PVC into 5/2-inch lengths. Make as many ¾ lengths as you have brushes and as many 3-inch lengths as you have chambered designs (if you are making them).

c. You will need to sand the edges of the 3-inch PVC after cutting with hacksaw.

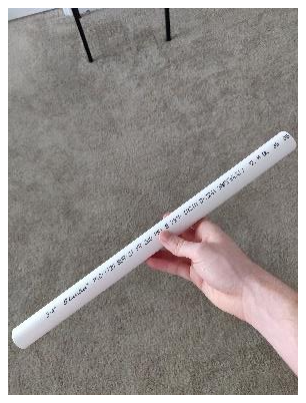
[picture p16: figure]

3. Seal cut ¾ inch PVC pipes with cling wrap and masking tape…
a. This is to prevent any leaking when applying epoxy to PVC pipes.
4. Prepare Brushes for Epoxy…

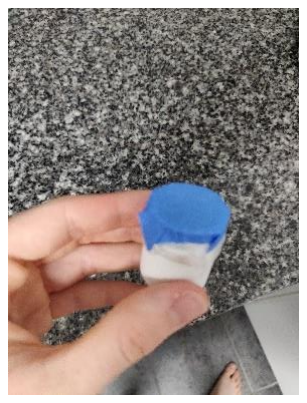
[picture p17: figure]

a. Zip tie the wire to the tip of the titanium brush stem. This will help keep the brush straight in the epoxy
b. Cut rectangles from old cardboard. Cut very slim slits into the cardboard that are just wide enough you can fit the brush stem into it, but it will not wiggle.
c. Slide brush into slit.
d. Add tape to the sides of the cardboard rectangle and allow them to curly upwards.
5. Prepare for Epoxy…
a. Create a workstation if you do not have one. I covered a living room table with old cardboard.
b. Follow directions on epoxy container to prepare desired amount.
6. Set in Epoxy…
a. Pour the epoxy into the open side of a ¾ inch PVC pipe segment leaving between ¼ inch and 1/8 inch from the top of the epoxy to the lip of the PVC pipe.
b. With one hand, firmly hold the PVC pipe while you use the other hand to place the cardboard-brush assembly into the center of the epoxy filling.

c. Firmly press down on the cardboard sides while making the tape taut between the cardboard and the workstation table.
d. After applying the tape, you can adjust the cardboard slightly to try and center the brush in the PVC pipe if it is not centered anymore.
e. Do one at a time to make sure you do not make a mistake! Repeat this for all your brushes.
7. Allow the brushes to cure for specified time on the epoxy directions…
8. After curing, remove the tape and cardboard from all the brushes. Remove all the tape and cling wrap as well…
a. Your finished product should resemble the pictures below. The picture on the right is the bottom view of the PVC.
9. Heat Shrinking the Electrode wire…

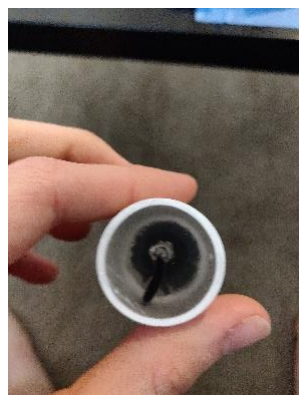
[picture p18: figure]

a. If you do not believe your wires will be long enough after the electrodes are inserted into their respective designs in an enclosure, this is an easy fix.
b. Simply strip the ends of the wire from the electrode and an additional wire length of your desired length. Twist the lengths around each other and solder them together.
c. Slide a heat shrink sleeve around the solder point and use the heat gun to fit it properly.
d. If you did not solder any additional wire lengths, I still HIGHLY RECOMMEND that you label your electrodes as cathodes and anodes using black and red heat shrink. You can ignore this if you have two wire colors and designated cathodes and anodes in step 1. If you are using the black wire I suggested, you only need to heat shrink the red sleeves onto the electrodes you are denoting as cathode. This will help you greatly in your organization.
10. Construct the Chambered Design… (Skip this if you are not following this design)
a. Insert a 3-inch PVC length into the 3-inch x 1.5-inch coupling.
b. Insert a 1.5 inch to ¾ inch bushing into the top of the coupling.
c. Insert a designated anode (see last step) wire into the bushing and feed it through.
d. Insert the anode PVC housing upside down so the brush is facing the bottom of the chamber.
e. Insert an elbow on the exposed ¾ inch PVC pipe.

f. Insert the cathode brush out of the elbow PVC pipe.

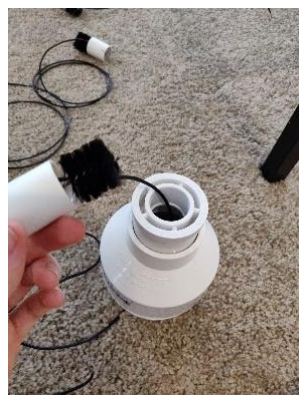
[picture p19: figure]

11. Construct the Unchambered design…
a. Use the pictures above as a guide.
b. Insert the back end of an anode PVC piece into an elbow or vertical PVC coupling.
c. Insert the back end of a cathode PVC piece into an elbow or vertical PVC coupling.
d. The finished design should look like a chamber design without the chamber in the first picture.
12. Add the quick connections…

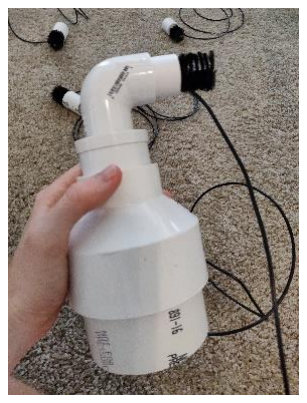
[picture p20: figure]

a. Add the quick connects to the ends of the anode and cathode wires. You MUST stay consistent with what end gets a plug and what end gets a socket. My cathodes always got the socket, and my anodes always got the plug.
b. If you are not consistent, it will make monitoring the fuel cells much more annoying, and it will make it impossible to connect all your cells in series!
c. If you purchased the connectors I recommended, here is how you apply the connectors:
i. If you are applying a plug (the piece you slide the wire into), strip the wire and twist the expose wire to make it easier to thread through the plug hole. Once inserted into the plug hole, crimp the plug with a set of pliers. ii. If you are applying a socket (the piece that is folded), simply place an unstripped wire into the metal prongs, and use the pliers to fold the piece over until it snaps.
d. Make sure you check these connections by making a dummy pair of quick connects that have a stripped end on the other side of the wire. You will also need these to test the voltage of the fuel cells in the future!

Indoor Deployment…

1. Assign your designs to their respective containers…
a. Label the containers with what variables they are assigned with.

b. For example, for a container using salt water, unchambered anode, and additive, I labeled it “S/U/A”

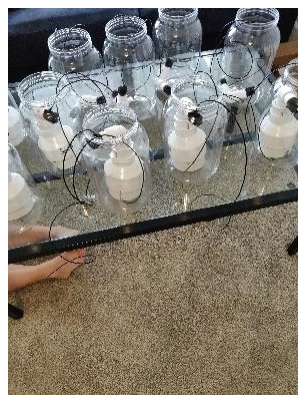
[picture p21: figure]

2. Figure out where you are putting the finished containers…
a. I used the same table that I cured the epoxy on.
b. I divided my table into sections using masking tape so that there were 10 sections on the table. (5 rows of 2)
c. Set up your air pumps so that they can reach the desired container. Use the power strip to plug the air pumps in so you can keep all the air pumps together.
d. I kept all my air pumps on one side of the table, and I had the tubing go between all the containers.
3. Gather your sediment and water samples…
a. I used the shovel to gather the sediment samples and placed it into a 17-gallon container.
b. I dipped the second container into the water directly to get the needed water samples.
c. Make sure to adjust your water sample with salt if you are varying salinity levels in different containers!
d. Make sure to homogenize the samples by stirring them!
4. Add the additive if needed…
a. If you are adding an additive to a container, insert a small amount of sediment on the bottom of the container and place the additive on top of that, twisting it into the sediment to secure its position.
5. Add the sediment into the container…
a. Fill the sediment up in each container to a uniform level. I added about 5 inches of sediment into the containers with unchambered electrodes, and about 4 inches of sediment into containers with chambered electrodes.
6. Constructing the chambered design container…
a. Add about 2 inches of water into the container.
b. Remove the anode PVC from the bushing on the chambered design so you have a chamber in one hand and essentially the unchambered design in the other hand. Make sure you keep the wire end through the chamber, so it looks like the second picture of step 10.
c. Insert the chamber into the sediment up until the point where if the brush is inserted, it would be slightly above the sediment. Always keep the quick connect out of the container! Do not take any chances and do not allow it to touch any water or sediment.
d. If the chamber is not under water at this point, add more water into the container until the entire chamber is under the water level.

e. Once the water is above the bushing hole, reinsert the anode into the bushing so that the design is one piece again.
f. Fill the container with water until it is at the top.
g. Use the masking tape to create a make-shift cap. Leave room to insert the air pump.
h. Insert the air pump and close the rest of the cap with more tape.
i. Repeat this with all your chambered designs.
7. Construct the unchambered design container…
a. Insert the anode directly into the sediment.
b. Always keep the quick connect out of the container! Do not take any chances and do not allow it to touch any water or sediment.
c. Fill the container with water.
d. Use the masking tape to create a make-shift cap. Leave room to insert the air pump.
e. Insert the air pump and close the rest of the cap with more tape.
f. Repeat this with all your unchambered designs.
8. You are done!
a. To check the voltage, I would take the dummy quick connects and attach it to the cathode and anode. I would then attach the gator clips to the stripped wire ends and the leads of the multimeter. Turn the multimeter on and you have your voltage reading! I did this twice a day for near a full month.
b. You can do a bunch of interesting tests like discharge and charging tests where you monitor the behavior of the fuel cell while and after draining the voltage.
c. Have fun!

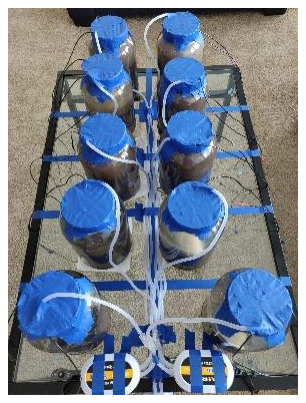
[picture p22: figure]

Outdoor Deployment…

1. Complete your Arduino enclosure…

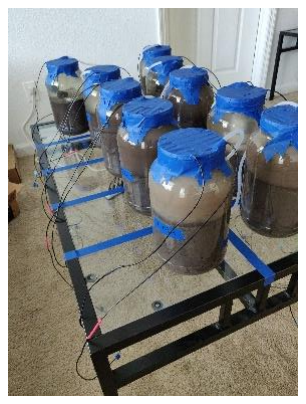
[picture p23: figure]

a. Your fuel cells should be soldered to the thruster wires, and your battery should be plugged in, so the Pro Mini is running the code that is uploaded.
2. Bring all your supplies to the chosen deployment site…
a. Choose your deployment site (I deployed very close to shore of a lake).
b. Bring your enclosure with fuel cells, a cinderblock, zip ties or something to fasten the enclosure to the cinderblock, and a PVC pipe length.
3. Attach the enclosure to the cinderblock…
a. I used the zip ties to attach the enclosure to the cinderblock to prevent the enclosure from floating.
4. Deploy the enclosure…
a. Insert the enclosure into the water and place it on the floor of the body of water.
5. Dig holes for fuel cells…

a. The sediment I was deploying in was compact, so I used a PVC pipe to dig holes which were made for the fuel cells.
6. Insert fuel cells into holes…
a. Insert the fuel cells into the freshly made holes…
b. Pack the dirt around the inserted fuel cell to secure it in place.
7. Leave for extended period…
a. Allow the device to gather data for the period that you decided. Mine was running for only a week due to the end of my project.
8. Retrieve the device and analyze the data…
a. Remove the enclosure and the fuel cells.
b. Remove the SD card and insert into computer.
c. Analyze data
9. You are done!

# Recommendations

This section is entirely dedicated to recommendations I have for someone who wants to replicate or continue the research seen in the project. You can take my recommendations or ignore them. After all, it is your project!

### General Recommendations

Variable Selection…
Variable selection is very important and will have a direct correlation to how many and what sized containers you would need for indoor fuel cells.

I personally think it would be interesting to see some data on various levels of salinity in fuel cell water instead of the two levels (freshwater and simulated ocean water) that I used.

I also think a promising idea would be introducing some type of chemical to the water or testing different additives to see how it effects the overall voltage. To be used in a in situ environment, the chemical/ additive would obviously need to be safe for animals, but you can ignore that in an indoor fuel cell.

Fuel Cell Design (Unchambered vs. Chambered) …
One of my largest regrets for my indoor fuel cells were using chambered anodes. I HIGHLY recommend against this. My reasoning for this is that they are significantly more difficult to deploy in a small container rather than an entire body of water. I will touch more on this in the next section. I believe that an indoor fuel cell should be unchambered, especially if using a relatively small enclosure.

If you are using 10-gallon fish tanks and you have a lot of room, then go for the chambered or unchambered. If you are working in 1-gallon containers like I was, then unchambered is the best option by far. The enclosure they are in is basically acting as a chamber due to how small the enclosure is, so adding a chamber to your anode is just going to make deployment and deconstruction more difficult.

If you are going to be in an in situ environment, then I highly recommend the chambered design; however, if you decide to use a chambered design, you should figure out a way to incorporate a check valve into the chamber. This is another very important design aspect I did not have the resources to do, and I wish I could have. This will prevent air bubble or even too much water in your chamber. This also allows for the escape of carbon dioxide.

Deployment is Key…
Now why do I recommend the chambered design in situ but the unchambered design for indoors? Deployment is the key here. If you do not properly deploy your fuel cells, there is a large chance the entire cell will not work. I have a strong belief that even if your fuel cell is deployed any way less than ideal, the voltages it will produce will suffer.

I recommend the unchambered design for an indoor enclosure because the sediment in an enclosure will be loose from homogenizing it, making it easy to insert the brush directly into the sediment. The chambered design is also very bulky, making it difficult to move around the enclosure when deploying it. This can lead to air bubbles stuck in the chamber (another reason for a check valve), which is not what you want. The harder to deploy, the less you want it.

I recommend the chambered design in situ mainly due to the more compact sediment found in the environment. You will not be uprooting and homogenizing sediment for a in situ deployment, meaning the sediment could very well be very compact. Trying to drive an anode directly into that hard sediment can lead to the harming or destroying of the anode before your data collection even begins. The chambered design is beneficial here since you are driving the chamber into the sediment, not the anode directly. The chamber will be easier to break into the hard sediment and should not be harmed in deployment.

When constructing you designs, deployment needs to be a top priority! MAKE SURE YOUR DESIGNS ARE NOT GOING TO FLOAT. ADD SAND INTO HOLLOW PVC PIPES. THIS AFFECTED MY DATA AS FUEL CELLS BEGAN TO DISLODGE FROM THE SEDIMENT DUE TO BOUYANCY.

### Indoor Deployment Recommendations

Data Collection and Analysis…
I was told by an expert in the field that I should always have connected the anode and cathode by a resistor. A very high resistance would be needed, but this would allow the fuel cell to continuously be creating power. Unfortunately, I was told this a little late into my project. I would recommend further looking into this idea, as I am not too certain about it. Something to think about!

Polarization Curves…
This is another of the larger regrets I have from my project. I never was able to construct a polarization curve. A polarization curve is what every literature paper based on BMFCs will have. You are going to want to construct multiple graphs relating to voltage, current density, and power density. To get the voltage data, you need to set up a fuel cell in series with a certain resistance and allow it to reach a stabilizing point (The red circle in the image below). That is where you take the voltage value with that resistance. You use the voltage and resistance to get the current and power. Those are used to get current and power density when compared to the anode surface area. Once again, I am almost certain this is how it works, but I never got a chance to do this. I would verify this is the correct way to do it before continuing forward with it; however, I highly recommend completing this.

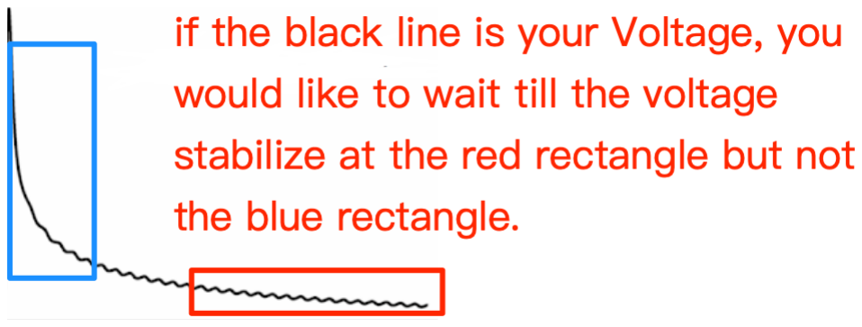
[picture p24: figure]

Oscillating Tests…
This is another thing I never got to do. This is by far the most difficult recommendation, as it would require some serious modification to any of the code and Arduino hardware to work. The idea is to have an Arduino circuit switch between discharging on a resistor and allowing a fuel cell to charge without any human intervention.

For this to work, you would need some knowledge on transistors (I think). My idea was to use transistors to switch between a resistor and no connection to allow the fuel cell to discharge on the resistor then recharge on an empty connection. I have created a rough idea of how I think the circuit would need to be built for this. It is on the GitHub. Only an idea though, so it may not work. Just to get you started…

# Closing Remarks

Well, here we are…

Do not worry, I do not have much else to add at this point.

I hope everything you needed was available to you in this packet. If you have any other questions, please reach out to Dr. Jordon Beckler or me, Emerick Gilliams. You can reach me at gilliamse@ufl.edu or 772-589-2628.

I hope you enjoyed learning about my project and how you can make your own!

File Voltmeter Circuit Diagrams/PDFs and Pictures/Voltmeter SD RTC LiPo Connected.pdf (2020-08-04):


The AA Battery is an example of how to test voltage


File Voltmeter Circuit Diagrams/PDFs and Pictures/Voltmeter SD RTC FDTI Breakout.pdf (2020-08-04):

GND VCC; MISO; MOSI SCK

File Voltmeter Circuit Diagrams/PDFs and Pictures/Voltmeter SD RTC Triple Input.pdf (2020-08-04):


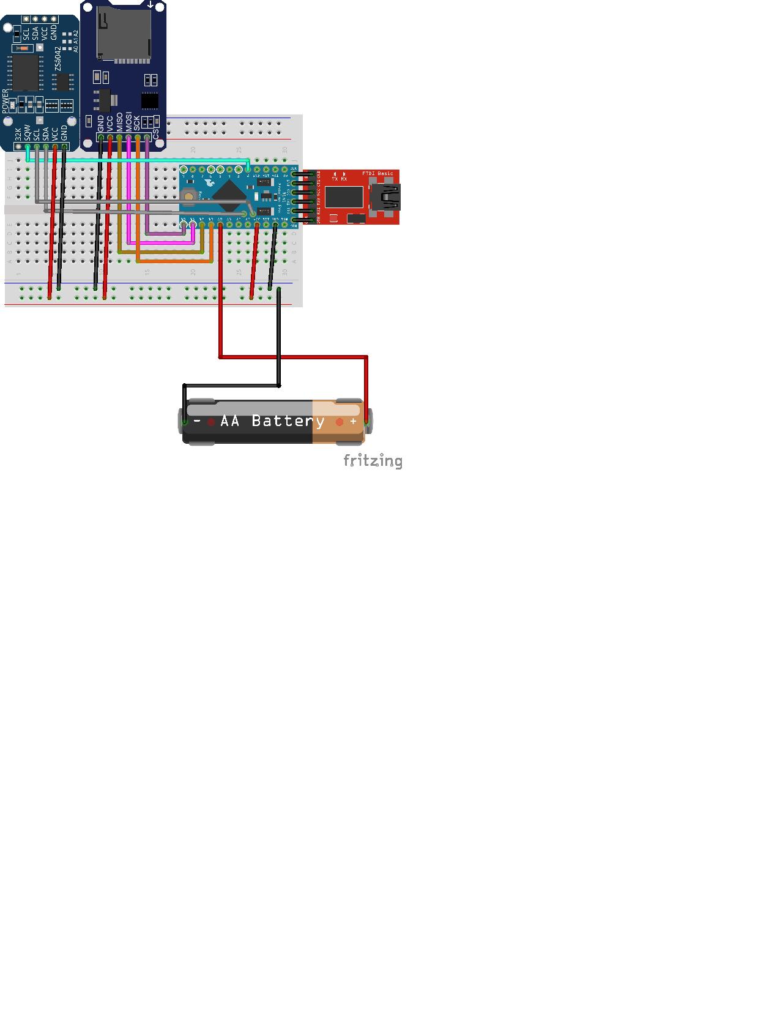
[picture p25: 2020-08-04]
Voltmeter Circuit Diagrams/PDFs and Pictures/Voltmeter SD RTC FDTI Breakout.jpg

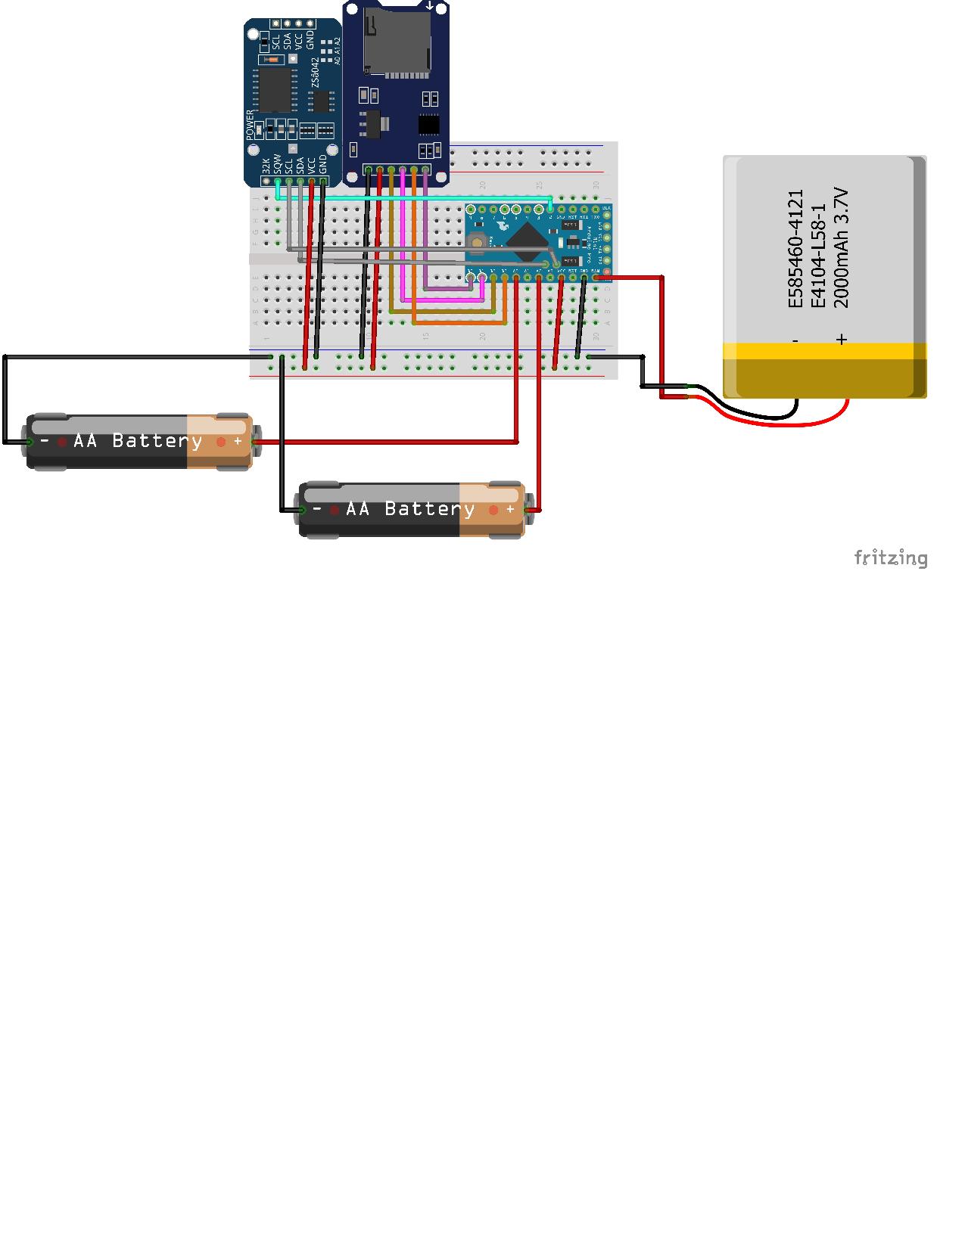
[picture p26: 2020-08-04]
Voltmeter Circuit Diagrams/PDFs and Pictures/Voltmeter SD RTC Double Input.jpg

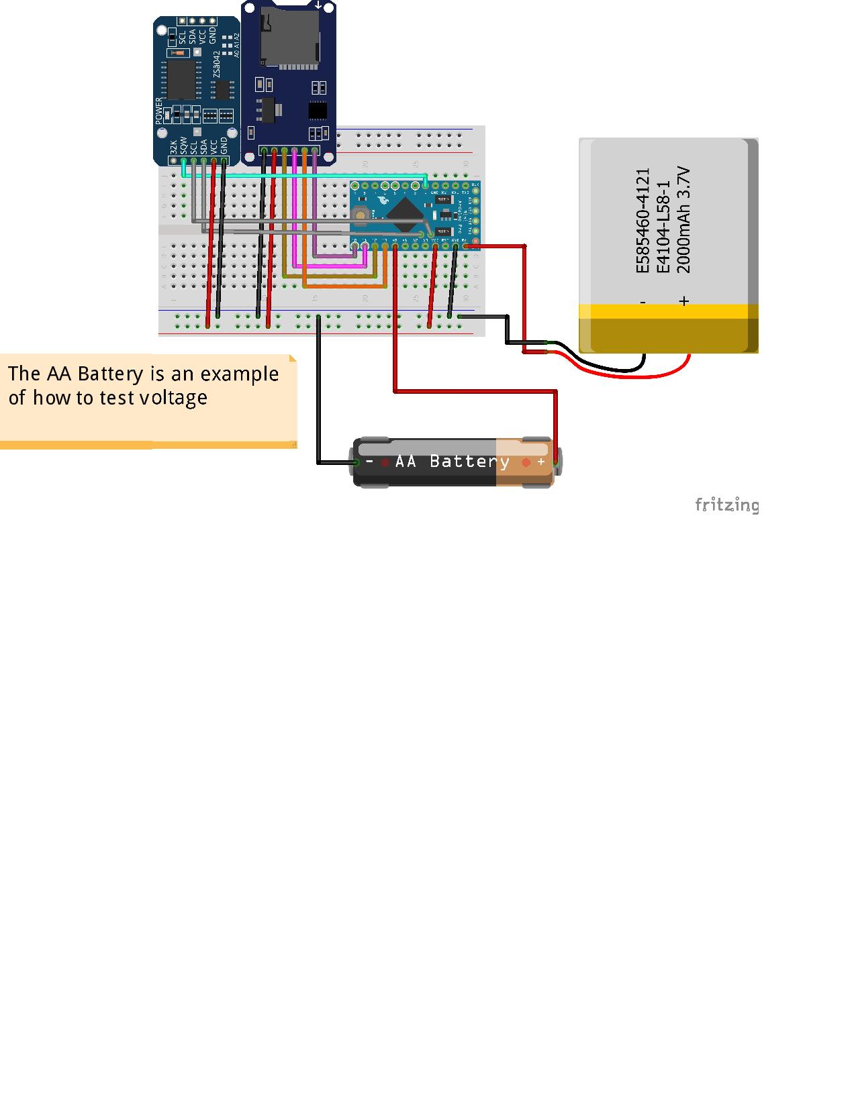
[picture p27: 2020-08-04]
Voltmeter Circuit Diagrams/PDFs and Pictures/Voltmeter SD RTC LiPo Connected.jpg

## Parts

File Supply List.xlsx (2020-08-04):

Supply List for Benthic Microbial Fuel Cell Project
MATERIALS FOR A DEPLOYABLE FUEL CELL
The Electrode System… | Quantity | Price | Total Price | Link
Electrode Brushes | 20 | $7.79 | $155.80 | https://www.millrose.com/carbon_fiber_brushes.php
Electrical Wire | 1 | $8.00 | $8.00 | https://www.amazon.com/Southwire-55667423-Primary-18-Gauge-100-Feet/dp/B003J699RW
Soldering kit | 1 | $25.00 | $25.00 | https://www.amazon.com/Soldering-Iron-Kit-Temperature-Screwdrivers/dp/B07GJNKQ8W?cv_ct_cx=soldering+kit
Quick Connector Kit | 1 | $12.00 | $12.00 | https://www.amazon.com/TICONN-Connectors-Self-Stripping-Electrical-Disconnect/dp/B07MLPBPW5
Epoxy | 1 | $45.00 | $45.00 | https://www.amazon.com/Casting-Countertop-Measuring-Plastic-Spreader/dp/B0834C5T12
Heat Shrink Tubing | 1 | $11.00 | $11.00 | https://www.amazon.com/270-pcs-Adhesive-Assortment-MILAPEAK/dp/B0771K1Z7Q?s=industrial
Heat Gun | 1 | $13.00 | $13.00 | https://www.amazon.com/ZeopoCase-caliente-port%C3%A1til-embalaje-termopl%C3%A1stico/dp/B073RK2M2Y?rnid=2661617011
Multimeter | 1 | $12.00 | $12.00 | https://www.amazon.com/AstroAI-Digital-Multimeter-Voltage-Tester/dp/B01ISAMUA6
Pack of AA Batteries | 1 | $9.00 | $9.00 | https://www.amazon.com/AmazonBasics-Performance-Alkaline-Batteries-20-Pack/dp/B00NTCH52W
Rosin Core Solder | 1 | $9.00 | $18.00 | https://www.amazon.com/MAIYUM-63-37-Solder-Electrical-Soldering/dp/B076QF1Y85?ac_md=1-0-VW5kZXIgJDEw-ac_d_pm&cv_ct_cx=rosin%2Bcore%2Bsolder&s=toys-and-games
Painters Tape | 1 | $3.50 | $3.50 | https://www.amazon.com/ScotchBlue-Painters-Multi-Use-70-Inch-2090-18E/dp/B00004Z4BB
Cling Wrap | 1 | $3.00 | $3.00 | amazon.com/Glad-Pressn-Seal-Food-Plastic/dp/B0014D5NVS/ref=sr_1_2_sspa?crid=2FUD36KJELNK2&dchild=1&fpw=pantry&keywords=cling+wrap&qid=1595614238&s=pantry&sprefix=cling+w%2Caps%2C185&sr=8-2-spons&psc=1&spLa=ZW5jcnlwdGVkUXVhbGlmaWVyPUEzS1hUMFlRSVVRUEJIJmVuY3J5cHRlZElkPUEwMTUzODMzMkNNQjJWUDg0UjZTQSZlbmNyeXB0ZWRBZElkPUEwMDg2MjkwM0c0VDY2TUFJQkFYQSZ3aWRnZXROYW1lPXNwX2F0ZiZhY3Rpb249Y2xpY2tSZWRpcmVjdCZkb05vdExvZ0NsaWNrPXRydWU=
Zip Ties | 1 | $4.00 | $4.00 | https://www.amazon.com/Superun-selflocking-cable-Industrial-grade/dp/B07P6JDW9L
Pliers | 1 | $9.00 | $9.00 | https://www.amazon.com/DOWELL-Linemans-Combination-Construction-Professional/dp/B07476LTSB?cv_ct_cx=pliers
3/4 inch x 10 ft PVC Pipe | 1 | $2.41 | $2.41 | In Person: Lowes
 |  | Total Price | $330.71
Fuel Cell PVC Design… | Quantity | Price | Total Price | Link
3/4 inch x 10 ft PVC Pipe | 1 | $2.41 | $2.41 | In Person: Lowes
3/4 inch elbow | 10 | $0.64 | $6.40 | In Person: Lowes
PVC pipe cutter | 1 | $14.98 | $14.98 | In Person: Lowes
3 inch x 2 ft PVC Pipe | 1 | $6.58 | $6.58 | In Person: Lowes
3 inch x 1.5 inch PVC Coupler | 6 | $4.58 | $27.48 | In Person: Lowes
1.5 inch x 3/4 inch bushing | 6 | $1.14 | $6.84 | In Person: Lowes
Hacksaw | 1 | $15.00 | $15.00 | In Person: Lowes
Sandpaper | 1 | $5.97 | $5.97 | In Person: Lowes
 |  | Total Price | $85.66
ARDUINO CIRCUITRY AND ENCLOSURE
Arduino Circuitry | Quantity | Price | Total Price | Link
Micro SD Card reader | 1 | $6.00 | $6.00 | https://www.amazon.com/dp/B07BJ2P6X6
Micro SD Card | 1 | $10.00 | $10.00 | https://www.amazon.com/Tarjetas-memoria-Micro-Clase-C10/dp/B07WG2RJV5?s=electronics
M-F, F-F, M-M Wires | 1 | $7.00 | $7.00 | https://www.amazon.com/dp/B01EV70C78/ref=twister_B07RWTHF6D?_encoding=UTF8&th=1
Pre-Formed Jumper Wire Kit | 1 | $6.00 | $6.00 | https://www.amazon.com/gp/product/B014JOV4TI/ref=ox_sc_saved_title_2?smid=A1LHQ5G6ONPXVT&psc=1
DS3231 Real Time Clock | 1 | $11.00 | $11.00 | https://www.amazon.com/HiLetgo-AT24C32-Arduino-Without-Battery/dp/B00LX3V7F0
Battery for DS3231 | 1 | $3.00 | $3.00 | https://www.amazon.com/Panasonic-CR2032-Lithium-Coin-Battery/dp/B07SNSXNSX
Arduino Pro Mini 3.3V 8Mhz | 1 | $13.00 | $13.00 | https://www.amazon.com/gp/product/B078HM2LC3/ref=ox_sc_act_title_1?smid=A2K4DGCC72N9AG&psc=1
Rosin Core Solder | 1 | $9.00 | $9.00 | https://www.amazon.com/MAIYUM-63-37-Solder-Electrical-Soldering/dp/B076QF1Y85?ac_md=1-0-VW5kZXIgJDEw-ac_d_pm&cv_ct_cx=rosin%2Bcore%2Bsolder&s=toys-and-games
Breadboards | 1 | $8.00 | $8.00 | https://www.amazon.com/dp/B08115P2T4
Lithium Polymer Battery Connector | 1 | $8.00 | $8.00 | https://www.amazon.com/Upgraded-Connector-Battery-Inductrix-Eachine/dp/B07NWD5NTN
Lithium Polymer Charger Circuit | 1 | $16.00 | $16.00 | https://www.sparkfun.com/products/12711
Lithium Polymer battery | 1 | $13.00 | $13.00 | https://www.sparkfun.com/products/13855
FDTI Breakout | 1 | $15.00 | $15.00 | https://www.sparkfun.com/products/9873
FDTI Cable | 1 | $4.00 | $4.00 | https://www.sparkfun.com/products/11301
Headerpins | 1 | $8.00 | $8.00 | https://www.amazon.com/gp/product/B01MQ48T2V/ref=ppx_yo_dt_b_search_asin_title?ie=UTF8&psc=1
 |  | Total Price | $137.00
Arduino Enclosure | Quantity | Price | Total Price | Link
Potting Kit | 1 | $10.00 | $10.00 | https://bluerobotics.com/store/cables-connectors/tools/tool-potting-kit-r1/
Marine Epoxy | 1 | $6.00 | $6.00 | https://bluerobotics.com/store/cables-connectors/tools/loctite-marine-epoxy/
M10 Cable Penetrator for 6mm Cable | 2 | $4.00 | $8.00 | https://bluerobotics.com/store/cables-connectors/penetrators/penetrator-10-25-a/
Penetrator Wrench | 1 | $13.00 | $13.00 | https://bluerobotics.com/store/cables-connectors/tools/tool-penetrator-wrench-r1/
M10 Cable Penetrator Blank (No Hole) | 3 | $4.00 | $12.00 | https://bluerobotics.com/store/cables-connectors/penetrators/penetrator-blank-10-25-a-r2/
1 Meter of Thruster Cable (3 conductors, 18 AWG) | 2 | $8.00 | $16.00 | https://bluerobotics.com/store/cables-connectors/cables/cab-a-3-18awg-r1/
200 mm of Customizable Cast Acrylic Tube (4″ Series) | 1 | $40.00 | $40.00 | https://bluerobotics.com/store/watertight-enclosures/4-series/wte4-p-tube-custom-r1/
Aluminum End Cap with 5 Holes (4″ Series) | 1 | $20.00 | $20.00 | https://bluerobotics.com/store/watertight-enclosures/4-series/wte4-m-end-cap-5-hole-r1/
O-Ring Flange (4″ Series) | 2 | $29.00 | $58.00 | https://bluerobotics.com/store/watertight-enclosures/4-series/wte4-m-flange-seal-r3/
Aluminum End Cap (4″ Series) | 1 | $16.00 | $16.00 | https://bluerobotics.com/store/watertight-enclosures/4-series/wte4-m-end-cap-r1/
Enclosure Vent and Plug | 1 | $9.00 | $9.00 | https://bluerobotics.com/store/cables-connectors/penetrators/vent-asm-r1/
Silicon Grease | 1 | $4.00 | $4.00 | https://www.amazon.com/Waterproof-Silicone-Grease-1-Pack-88693/dp/B000DZFUPC
Hex Driver | 1 | $5.00 | $5.00 | https://www.amazon.com/Bondhus-12592-GorillaGrip-Fold-up-1-5-6mm/dp/B0006O4AG0
Exacto Knife | 1 | $7.00 | $7.00 | https://www.amazon.com/X-Acto-XZ3601-X-ACTO-Knife-Safety/dp/B005KRSWM6?s=office-products
 |  | Total Price | $224.00
MATERIALS FOR FUEL CELL DEPLOYMENT
Variable | Quantity | Price | Total Price | Link
Salt | 1 | $2.00 | $2.00 | In Person: Walmart
Vacation Fish Food | 6 | $3.00 | $18.00 | https://www.amazon.com/API-VACATION-PYRAMID-1-2-Ounce-Automatic/dp/B00025Z66G
 |  | Total Price | $20.00
Indoor Deployment | Quantity | Price | Total Price | Link
Deployable Fuel Cell | 10 | N/A | N/A | N/A
Plastic Containers | 5 | $16.00 | $80.00 | https://www.amazon.com/Pinnacle-Mercantile-Crystal-Plastic-Containers/dp/B01MXY7UU9
Air Pumps | 5 | $15.00 | $75.00 | https://www.amazon.com/Uniclife-Aquarium-Outlet-Accessories-Gallon/dp/B07WC8HNKN
Power Strip | 1 | $11.00 | $11.00 | https://www.amazon.com/AmazonBasics-6-Outlet-Surge-Protector-6-Foot/dp/B00TP1C51M
Painters Tape | 1 | $3.50 | $3.50 | https://www.amazon.com/ScotchBlue-Painters-Multi-Use-70-Inch-2090-18E/dp/B00004Z4BB
Shovel | 1 | $10.98 | $10.98 | In Person: Lowes
Large Containers | 2 | $9.48 | $18.96 | In Person: Lowes
Multimeter | 1 | $12.00 | $12.00 | https://www.amazon.com/AstroAI-Digital-Multimeter-Voltage-Tester/dp/B01ISAMUA6
Alligator Clips | 1 | $5.00 | $5.00 | https://www.amazon.com/KAIWEETS-Electrical-Alligator-Connection-Experiment/dp/B07WQ21YMY
Potentiometer Kit | 1 | $7.00 | $7.00 | https://www.amazon.com/MCIGICM-Potentiometer-Linear-WH148-Shaft/dp/B0791GYLBZ
Completed Arduino Circuit | 1 | N/A | N/A | N/A
 |  | Total Price | $223.44
Outdoor Deployment | Quantity | Price | Total Price | Link
Deployable Fuel Cell | 10 | N/A | N/A | N/A
Completed Arduino Circuit | 1 | N/A | N/A | N/A
Completed Arduino Enclosure | 1 | N/A | N/A | N/A
Cinderblock | 1 | $2.00 | $2.00 | In Person: Lowes
Something to loosen the sediment (3/4 PVC pipe) | 1 | $2.41 | $2.41 | In Person: Lowes
 |  | Total Price | $4.41

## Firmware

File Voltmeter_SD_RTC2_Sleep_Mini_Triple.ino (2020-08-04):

/*
 * This setup allows you to measure the voltage of three objects (Fuel Cells, Batteries, etc.) up to 3000 mV. 
 * The setup is currently calibrated to measure once every 10 minutes and goes to low power sleep when not actively measuring anything.
 * Calibrate the Cali variable to the voltage of the VCC pin that is going to the breadboard. 
 * 
 */


#include <Time.h>
#include <TimeLib.h>
#include <DS3232RTC.h>
#include <SD.h>
#include <SPI.h>
#include <avr/sleep.h> //this AVR library contains the methods that controls the sleep modes
#define interruptPin 2 //Pin we are going to use to wake up the Arduino

//Calibration from VCC
//float Cali = 3.36; // USB
float Cali = 3.28; // LiPo

//Files
File voltData;

//Pin Values
int pinCS = 10; //SD Card

//Variables for Timed Events
const unsigned long eventTime_1_Volt = 300; // in ms
const unsigned long eventTime_2_SD = 2100;

unsigned long previousTime_1 = 0;
unsigned long previousTime_2 = 0;

//Voltmeter Variables
float input_voltage = 0.0;
float input_voltage2 = 0.0;
float input_voltage3 = 0.0;
float temp=0.0;

//RTC Module global variables
const int time_interval=10;  // Sets the wakeup interval in minutes

// -#-#-#-#-#-#-#-#-#-#-#-#-#-#-#-#-#-#-#-#-#-#-#-#-#-#-#-#-#-#-#-#-#-#-#-#-#-#-#-#-#-#-#-#-#-#-#-#-#-#-#-# //
//                                                            SETUP
// -#-#-#-#-#-#-#-#-#-#-#-#-#-#-#-#-#-#-#-#-#-#-#-#-#-#-#-#-#-#-#-#-#-#-#-#-#-#-#-#-#-#-#-#-#-#-#-#-#-#-#-# //

 
void setup()
{
  //---------------------------------------------------SERIAL and SLEEP---------------------------------------------------//
  Serial.begin(9600);     //  opens serial port, sets data rate to 9600 bps
  pinMode(LED_BUILTIN,OUTPUT);//We use the led on pin 13 to indecate when Arduino is A sleep
  pinMode(interruptPin,INPUT_PULLUP);//Set pin d2 to input using the buildin pullup resistor
  digitalWrite(LED_BUILTIN,HIGH);//turning LED on


  //----------------------------------------------------------RTC----------------------------------------------------------//
  
  // initialize the alarms to known values, clear the alarm flags, clear the alarm interrupt flags. DO NOT TOUCH
  RTC.setAlarm(ALM1_MATCH_DATE, 0, 0, 0, 1);
  RTC.setAlarm(ALM2_MATCH_DATE, 0, 0, 0, 1);
  RTC.alarm(ALARM_1);
  RTC.alarm(ALARM_2);
  RTC.alarmInterrupt(ALARM_1, false);
  RTC.alarmInterrupt(ALARM_2, false);
  RTC.squareWave(SQWAVE_NONE);
  
  /*
   * JUST USE THE SERIAL SET UP EXAMPLE
   * 
   * Uncomment the block block to set the time on your RTC. Remember to comment it again 
   * otherwise you will set the time at everytime you upload the sketch
   * /
   /* Begin block *_///<---- Delete underscore to edit
   tmElements_t tm;
  tm.Hour = 16;               // set the RTC to an arbitrary time
  tm.Minute = 59;
  tm.Second = 30;
  tm.Day = 5;
  tm.Month = 6;
  tm.Year = 2020;      // tmElements_t.Year is the offset from 1970. DOESN'T WORKKKKK
  RTC.write(tm);              // set the RTC from the tm structure
   //Block end * */
  
  time_t t; //create a temporary time variable so we can set the time and read the time from the RTC
  t=RTC.get();//Gets the current time of the RTC
  RTC.setAlarm(ALM1_MATCH_MINUTES , 59, minute(t)+time_interval, 0, 0);// Setting alarm 1 to go off 10 minutes from now
  //RTC.setAlarm(ALM1_MATCH_MINUTES , 59, 0, 0, 0);// Setting alarm 1 to go off at the top of the next hour.
  // clear the alarm flag
  RTC.alarm(ALARM_1);
  // configure the INT/SQW pin for "interrupt" operation (disable square wave output)
  RTC.squareWave(SQWAVE_NONE);
  // enable interrupt output for Alarm 1
  RTC.alarmInterrupt(ALARM_1, true);

  //----------------------------------------------------------SD----------------------------------------------------------//
  pinMode(pinCS, OUTPUT); //Setting Pin
  
  if (SD.begin())
  {
    Serial.println("SD card is ready to use.");
  
  //Setup the File for Data  
    voltData = SD.open("VoltData.txt", FILE_WRITE);
  
    // If the file opened, write to it:
    if (voltData) {
      // Write to file
      voltData.print("Date");
      voltData.print(",    ");
      voltData.print("Time");
      voltData.print(",     ");
      voltData.print("Voltage (A0)");
      voltData.print(", ");
      voltData.print("Voltage (A1)");
      voltData.print(", ");
      voltData.println("Voltage (A2)");
      voltData.close();}
  } 
  else
  {
    Serial.println("SD card initialization failed");
    return;
  }
  
}

// -#-#-#-#-#-#-#-#-#-#-#-#-#-#-#-#-#-#-#-#-#-#-#-#-#-#-#-#-#-#-#-#-#-#-#-#-#-#-#-#-#-#-#-#-#-#-#-#-#-#-#-# //
//                                                   LOOP
// -#-#-#-#-#-#-#-#-#-#-#-#-#-#-#-#-#-#-#-#-#-#-#-#-#-#-#-#-#-#-#-#-#-#-#-#-#-#-#-#-#-#-#-#-#-#-#-#-#-#-#-# //

void loop()
{
// Updates constantly
  unsigned long currentTime = millis();
  
//Event 1  
  if(currentTime - previousTime_1 >= eventTime_1_Volt){
  
//Conversion formula for voltage
//Change the 3.35 to whatever the voltage is coming from the VCC pin onto the breadboard. 
   
    int analog_value = analogRead(A0);
    input_voltage = (analog_value * (Cali)*1000) / 1024.0;
    int analog_value2 = analogRead(A1);
    input_voltage2 = (analog_value2 * (Cali)*1000) / 1024.0; 
    int analog_value3 = analogRead(A2);
    input_voltage3 = (analog_value3 * (Cali)*1000) / 1024.0; 
   
    if (input_voltage < 0.01) 
    {
      input_voltage=0.0;
    } 
    if (input_voltage2 < 0.01) 
    {
      input_voltage2=0.0;
    }
    if (input_voltage3 < 0.01) 
    {
      input_voltage3=0.0;
    }

    Serial.print("mV = ");
    Serial.print(input_voltage);
    Serial.print(", ");
    Serial.print(input_voltage2);
    Serial.print(", ");
    Serial.println(input_voltage3);
    
    //Reset the clock
    previousTime_1 = currentTime;
  }
  //--------------------------------------------------------------SD START---------------------------------------------------------------//
  
//Event 2  
  if(currentTime - previousTime_2 >= eventTime_2_SD){

  tmElements_t tmCurr; //tmCurr is just a variable to hold current time
  time_t tCurr;
  RTC.read(tmCurr);
  tCurr = makeTime(tmCurr);
  
  int a = day(tCurr);
  String d;
  d = String(a); 
  
  // Create/Open file 
  if (day(tCurr) < 10) {
    voltData = SD.open("0"+d+monthShortStr(month(tCurr))+"20.txt", FILE_WRITE);
  }
  else {
    voltData = SD.open(d+monthShortStr(month(tCurr))+"20.txt", FILE_WRITE);
  }
  if (voltData.available() == 0) {
    
  }

  //----------------------------------------------------------SD REPORT OF DATA----------------------------------------------------------//
  
  // If the file opened, write to it:
  if (voltData) {
    // Write to file
    

    
    voltData.print(month(tCurr));
    voltData.print("/");
    voltData.print(day(tCurr));
    voltData.print("/");
    voltData.print(year(tCurr));
    voltData.print(", ");
    
    voltData.print(hour(tCurr));
    voltData.print(":");
    voltData.print(minute(tCurr));
    voltData.print(":");
    voltData.print(second(tCurr));
    voltData.print(", ");
    
    voltData.print(input_voltage);
    voltData.print(", ");
    voltData.print(input_voltage2);
    voltData.print(", ");
    voltData.println(input_voltage3);
    voltData.close();
    
    Serial.print("Written to file: ");
    
  //----------------------------------------------------------SERIAL REPORT OF DATA----------------------------------------------------------//
    
    Serial.print(month(tCurr));
    Serial.print("/");
    Serial.print(day(tCurr));
    Serial.print("/");
    Serial.print(year(tCurr));
    Serial.print(", ");
    
    Serial.print(hour(tCurr));
    Serial.print(":");
    Serial.print(minute(tCurr));
    Serial.print(":");
    Serial.print(second(tCurr));
    Serial.print(", ");
    
    Serial.print(input_voltage);
    Serial.print(", ");
    Serial.print(input_voltage2);
    Serial.print(", ");
    Serial.println(input_voltage3);
  }
  
  // If the file didn't open, print an error:
  else {
    Serial.println("error opening file");
  }

  Going_To_Sleep();
  
    
  //Reset the clock
  previousTime_2 = currentTime;
  }
}

void Going_To_Sleep(){
    sleep_enable();//Enabling sleep mode
    attachInterrupt(0, wakeUp, LOW);//attaching a interrupt to pin d2
    set_sleep_mode(SLEEP_MODE_PWR_DOWN);//Setting the sleep mode, in our case full sleep
    digitalWrite(LED_BUILTIN,LOW);//turning LED off
    time_t tUp;// creates temp time variable
    tUp=RTC.get(); //gets current time from rtc
    Serial.println("Sleep  Time: "+String(hour(tUp))+":"+String(minute(tUp))+":"+String(second(tUp)));//prints time stamp on serial monitor
    delay(500); //wait 1/2 second to allow the led to be turned off before going to sleep
    sleep_cpu();//activating sleep mode
    
    //Interrupt occurs from alarm and wakes up Arduino
    digitalWrite(LED_BUILTIN,HIGH);//turning LED on
    time_t tDown;
    tDown=RTC.get();
    Serial.println("WakeUp Time: "+String(hour(tDown))+":"+String(minute(tDown))+":"+String(second(tDown)));//Prints time stamp 
    //Set New Alarm
    
    int NewTime;
    NewTime = minute(tDown) + time_interval;
    if (NewTime >= 60) {
      NewTime = NewTime - 60;
    }
    
    RTC.setAlarm(ALM1_MATCH_MINUTES , 59, NewTime, 0, 0);
  
  // clear the alarm flag
  RTC.alarm(ALARM_1);
  }

void wakeUp(){
  Serial.println("Interrrupt Activated");//Print message to serial monitor
   sleep_disable();//Disable sleep mode
  detachInterrupt(0); //Removes the interrupt from pin 2;
 
}

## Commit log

2020-07-15 Add files via upload
    This variation allows you to measure the voltage of two different items (fuel cells, batteries, etc.). The current setup has the measurements taken every minute. This can be changed by adjusting the 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
2020-07-28 Add files via upload
    This shows how to connect three fuel cells.
    [Voltmeter SD RTC Triple Battery.fzz]
2020-07-28 Create How to Calibrate Voltmeter
